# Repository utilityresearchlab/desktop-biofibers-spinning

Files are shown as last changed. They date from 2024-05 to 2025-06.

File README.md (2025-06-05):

# Desktop Biofibers Spinning Machine v1.0.1

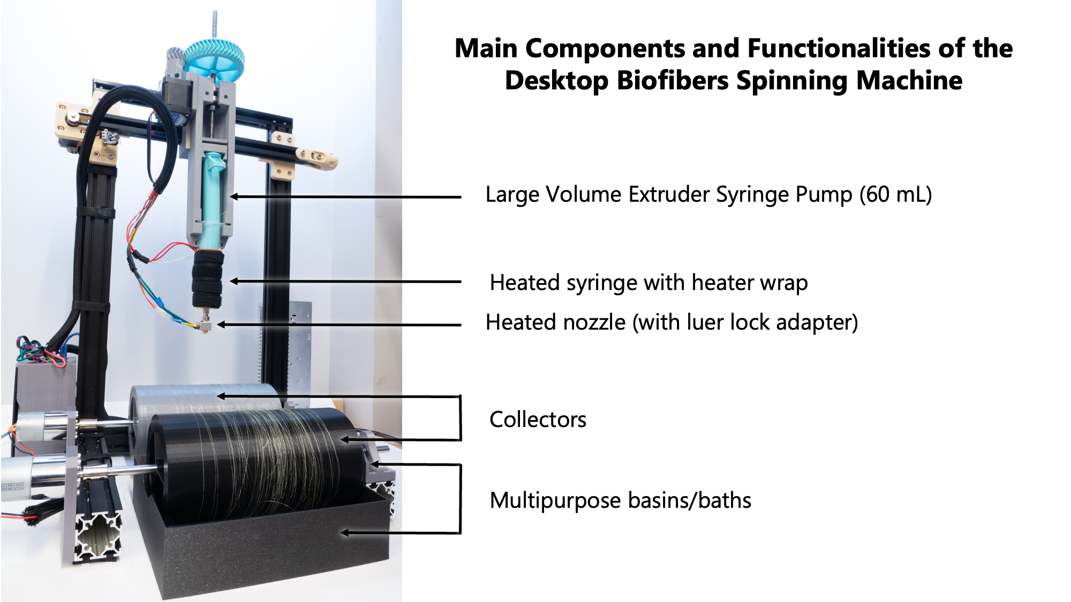
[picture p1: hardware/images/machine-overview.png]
Machine Overview


The Desktop Biofibers Spinning Machine is an open-source, modular machine for producing textile fibers from sustainable bio-based liquid solutions. It enables prototyping new types of sustainable fibers and exploring the design of sustainable smart textiles.

It supports spinning fibers from bio-based solutions, including ones that require heat during the spinning process. 

This repository contains all the design-related details and files to build the machine.

## High-level Specifications
- ~$600 for a machine (and even less if you reuse an old 3D printer like an Ender 3v2!)
- Heated Syringe Wrap
- 60 mL Syringe Volume (using the Open-Source Large Volume Extruder)
- Supports Luer Lock Nozzles/Tips
- Supports Heated Nozzle using a Luer Lock-to-M6 3D printer nozzle adapter
- Modular collector assemblies for applying different coatings to fibers

## Building a Biofibers Machine
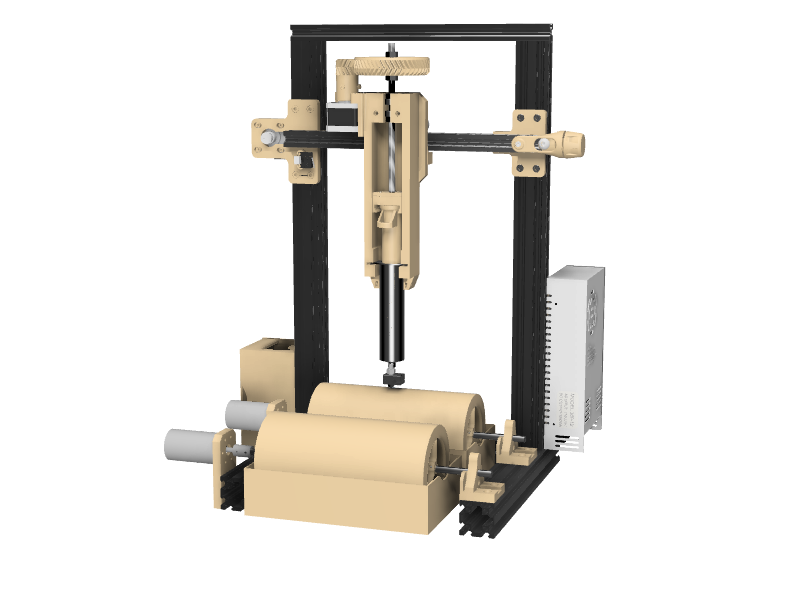
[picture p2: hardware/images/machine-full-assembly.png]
Machine Diagram with Printed Parts in Tan


- [Bill of Materials](https://docs.google.com/spreadsheets/d/1E_2IHzlC_cG40hGRjpHroCwSM1nkIKEBkRHdSb38-pU/edit#gid=0)
- Download the repository
- 3D Print the parts as listed in the BoM. Unless otherwise noted in the BoM Description/Notes, all 3D printed parts should be printed using PLA, 20% infill, 0.2 mm Layer height. The default "quality" setting in Prusa Slicer for the MK3S+/mini+ should be sufficient. The printed parts are shown in the color tan in the diagram above.

- Download the [CAD Assembly for Fusion 360](https://drive.google.com/drive/folders/1Qh19Er5d5Sq22oTk4Mabvu63gKj0vlPQ?usp=sharing) for assembly guidance and connect with us on Discord (see info below)
- Follow the [Electronics Wiring Diagram](https://github.com/utilityresearchlab/desktop-biofibers-spinning/blob/main/hardware/electronics-assembly/biofibers-electronics-wiring-diagram-v1.0.1.jpg) alongside the
  [RAMPS 1.4 Pin Out Schematic](https://github.com/utilityresearchlab/desktop-biofibers-spinning/blob/main/hardware/electronics-assembly/RAMPS%201.4/RAMPS1.4-PinOut-Schematic.png).

Electronics Wiring Diagram for the Biofibers Machine

- Follow our [work-in-progress assembly guide](https://docs.google.com/document/d/1JrAbMuTHmfADzdMDxia9Z5dNtl7umH7gnYQXavgpXdA/edit?tab=t.0#heading=h.pwn6s3sev8zz) for more instructions. 

## Using the Machine
We first recommend reviewing our [research paper](https://utilityresearchlab.org/assets/research/desktop-biofibers-spinning/chi24-desktop-biofibers-spinning.pdf) for more details on the fiber spinning process before using the machine.

To control the machine, we highly suggest using our open-source tool for MacOS and Windows available on our [Biofibers Machine Control repository](https://github.com/utilityresearchlab/biofibers-machine-control/). It streamlines setting up the machine as well as performing pull downs and the spinning procedure. You can do all of this without writing any g-code commands!

Screenshot 2025-05-24 at 10 03 42 PM

Alternatively, you may use any 3D printer host controller software like [Repetier Host](https://www.repetier.com/download-software/) to communicate with the machine. In your host controller software, set the baud rate to `250000`, and connect as you would a typical 3D printer. You can then use g-code commands to set the temperature of the syringe heater and nozzle, as well as set the collector speed/direction. More details are in the paper linked above.
   
## Join Our Discord for Assembly Help and Collaborations
We're eager to help and collaborate 😃! If you would like to work with us on the machine, build one yourself, or explore bio-based material solutions for fiber spinning, join our Discord: [https://discord.gg/vDmk3t2FMX](https://discord.gg/vDmk3t2FMX). For all other inquires, please reach out to 
 reach out to [Dr. Michael Rivera](https://mikeriv.com) and the [Utility Research Lab](https://utilityresearchlab.org).
 
## Planned Updates
- Movable Z-Axis
- ~Software Tool for Machine Control (for now a 3D printer host controller works to send G-code commands)~
- Custom Collector Shapes
- Assembly guides - [WIP Guide Here](https://docs.google.com/document/d/1JrAbMuTHmfADzdMDxia9Z5dNtl7umH7gnYQXavgpXdA/edit?tab=t.0#heading=h.pwn6s3sev8zz)

## Machine Design Change Log
- v1.0.1:
    - 2025-05-24:
      - Release Machine Control Desktop Application for MacOS and Windows    
    - 2024-11-30:
        - Added Electronics Wiring Diagram
    - 2024-11-07: 
        - Added new collector spindle v2.0.0 design with a key shaft lock
        - Added new LVE Small Gear v2 design
- v1.0.0: Initial design

## Paper Reference 
```
Eldy S. Lazaro Vasquez, Mirela Alistar, Laura Devendorf, and Michael L. Rivera. 2024. Desktop Biofibers Spinning: An Open-Source Machine for Exploring Biobased Fibers and Their Application Towards Sustainable Smart Textile Design. In Proceedings of the CHI Conference on Human Factors in Computing Systems (CHI '24). Association for Computing Machinery, New York, NY, USA, Article 856, 1–18. https://doi.org/10.1145/3613904.3642387
```

## Acknowledgements
This work is partially supported by the National Science Foundation under [Grant #241361](https://www.nsf.gov/awardsearch/showAward?AWD_ID=2413631&HistoricalAwards=false), [Grant #1943109](https://www.nsf.gov/awardsearch/showAward?AWD_ID=1943109&HistoricalAwards=false), and under Grant #2127309 to the
Computing Research Association for the CIFellows 2021 Project.
We are grateful to Simon Kammler, Daniel Wolters, Maximilian
Mohr, Stefan Peterek, Dr. Kazim Acatay, and research assistants at
the Institut für Textiltechnik (ITA) of RWTH Aachen University for
working with us as we explored fiber wet-spinning in their facilities. We are thankful to Philipp R. Stoessel for explaining his previous work with gelatin fibers wet spinning in very simple words which allowed us to replicate his spinning solution formulation. We would also like to acknowledge the support of Miles Henry Lewis who helped with designing and 3D printing the very first version of this machine.

### Open Source Projects
This machine leverages several open-source projects including the [RepRap RAMPS 1.4](https://reprap.org/wiki/RAMPS_1.4) under GPL v3 License, the [Marlin 2.1.1 firmware](https://marlinfw.org/) under GPL license, the [Large Volume Extruder](https://3d.nih.gov/entries/3DPX-008366) under CC-BY-SA 4.0, and the [Ender 3 V2 X axis belt tensioner replacement](https://www.printables.com/model/309148-ender-3-v2-x-axis-belt-tensioner-replacement) under CC-BY-NC-SA 4.0. The associated licenses can be found in the relevant folders of this repository.
##

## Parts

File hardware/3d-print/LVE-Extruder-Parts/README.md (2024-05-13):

# Original LVE Design is from https://3d.nih.gov/entries/3DPX-008366

# License: https://creativecommons.org/licenses/by-sa/4.0/

# Changes:
- Redesigned the Small gear (LVE_Small_Gear_v2.stl) to have a D-shaft and drop-in M3 nuts for a more secure fit.

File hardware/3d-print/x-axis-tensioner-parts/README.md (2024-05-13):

Original Design is "Ender 3 V2 X axis belt tensioner replacement" on Printables: 

- https://www.printables.com/model/309148-ender-3-v2-x-axis-belt-tensioner-replacement

- License: https://creativecommons.org/licenses/by-nc-sa/4.0/

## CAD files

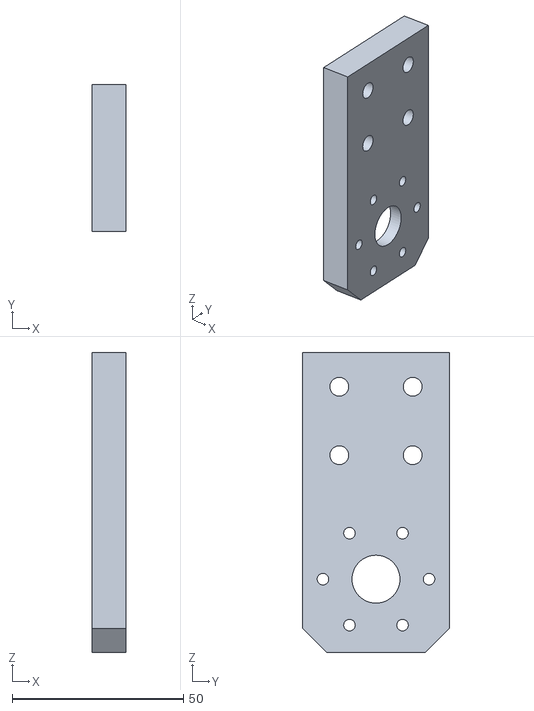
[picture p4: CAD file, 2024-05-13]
hardware/3d-print/collector-assembly/DC-Motor-Vertical Mount-10_RPM.stl
10.0 x 42.9 x 87.6

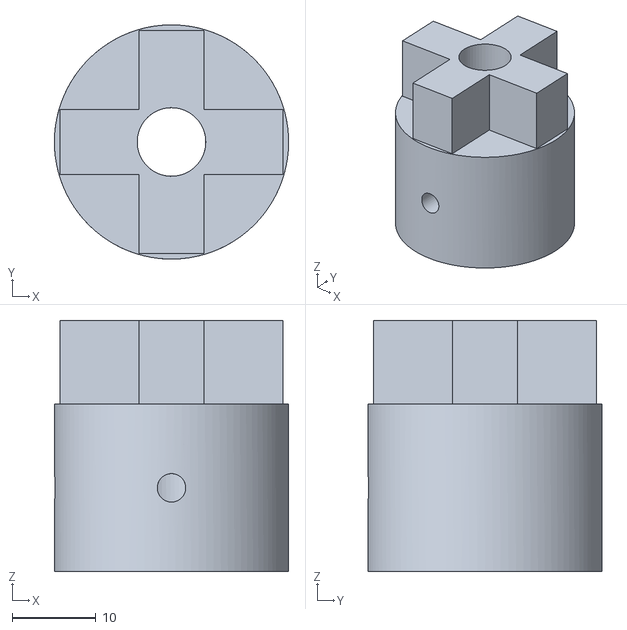
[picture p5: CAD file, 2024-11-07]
hardware/3d-print/collector-assembly/spindle-collector-v2.0.0/spindle-collector-_key-shaft-lock-v2.0.0.stl
28.0 x 28.0 x 30.0

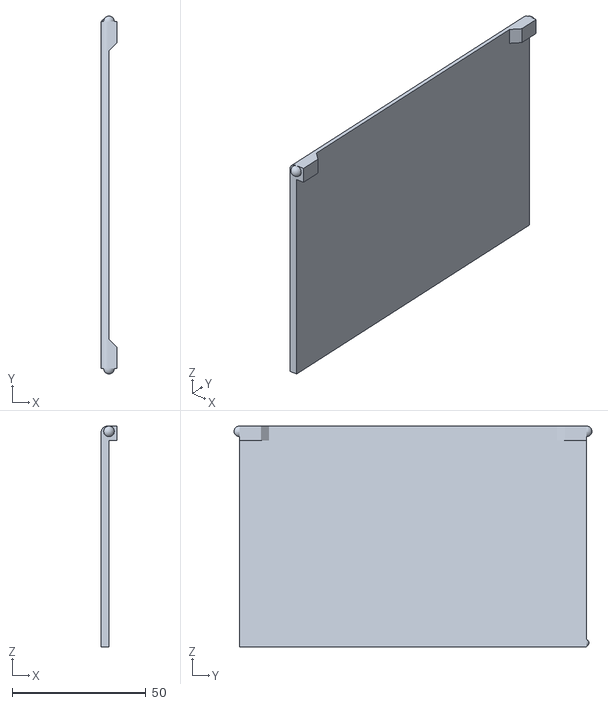
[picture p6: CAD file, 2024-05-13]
hardware/3d-print/electronics-enclosure/ramps-1.4-enclosure-door.stl
6.00 x 133.6 x 82.5

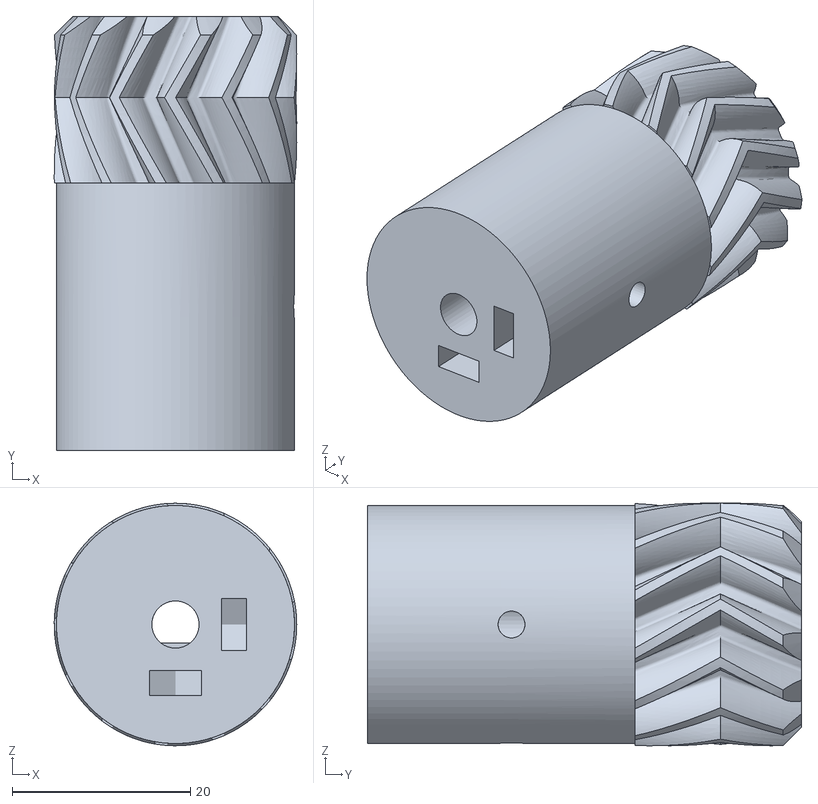
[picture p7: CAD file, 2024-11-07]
hardware/3d-print/LVE-Extruder-Parts/LVE_Small_Gear-v2.stl
27.2 x 48.7 x 27.2

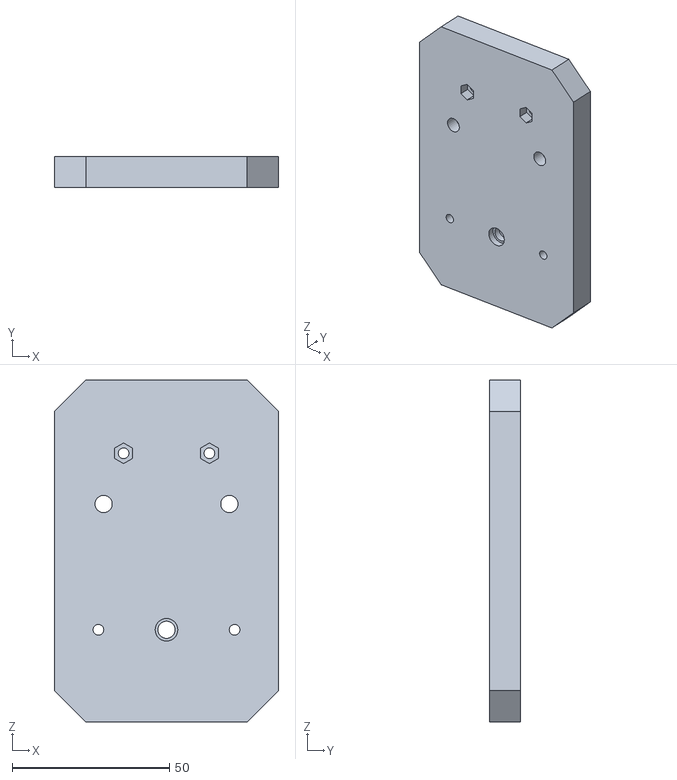
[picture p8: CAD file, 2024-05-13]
hardware/3d-print/x-axis-carriage/x-axis-carriage-syringe-adapter-v1.stl
71.3 x 10.0 x 108.8

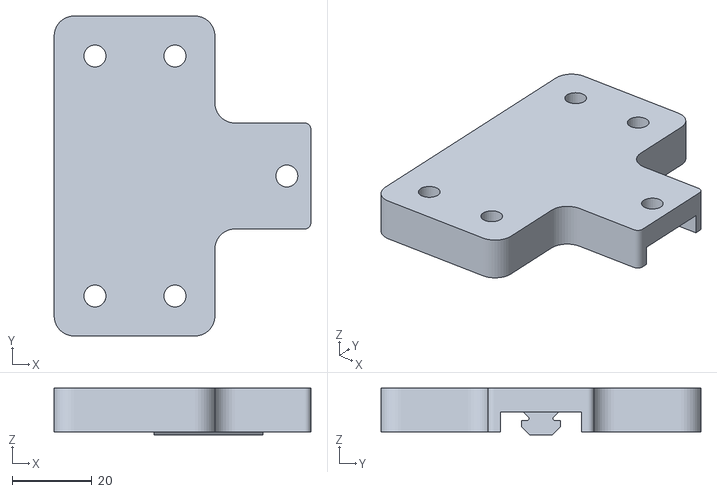
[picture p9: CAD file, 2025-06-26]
hardware/3d-print/x-axis-mount-right.stl
64.2 x 80.0 x 11.7

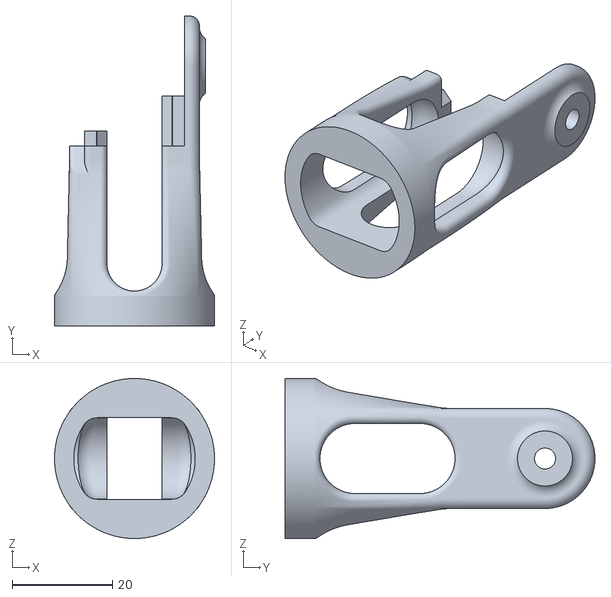
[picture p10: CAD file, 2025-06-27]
hardware/3d-print/x-axis-tensioner-parts/x-tensioner-body.stl
32.0 x 62.0 x 32.0

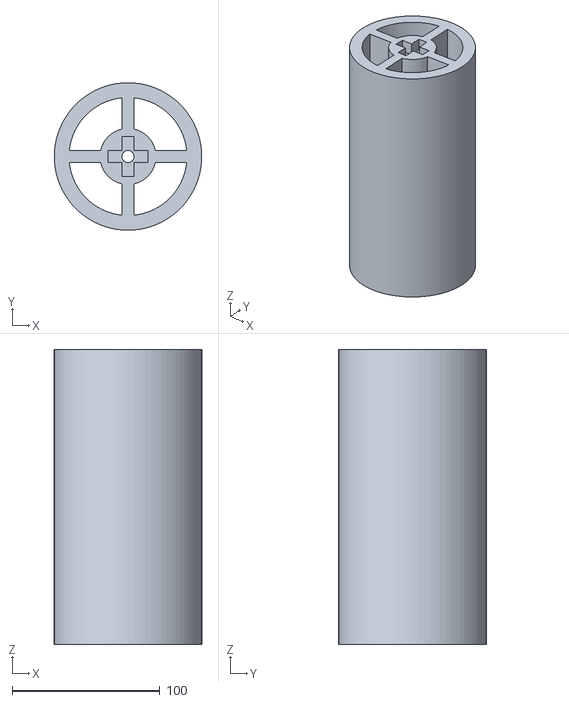
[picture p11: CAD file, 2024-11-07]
hardware/3d-print/collector-assembly/spindle-collector-v2.0.0/spindle-collector-keyed-body-v2.0.0.stl
100.0 x 100.0 x 200.0

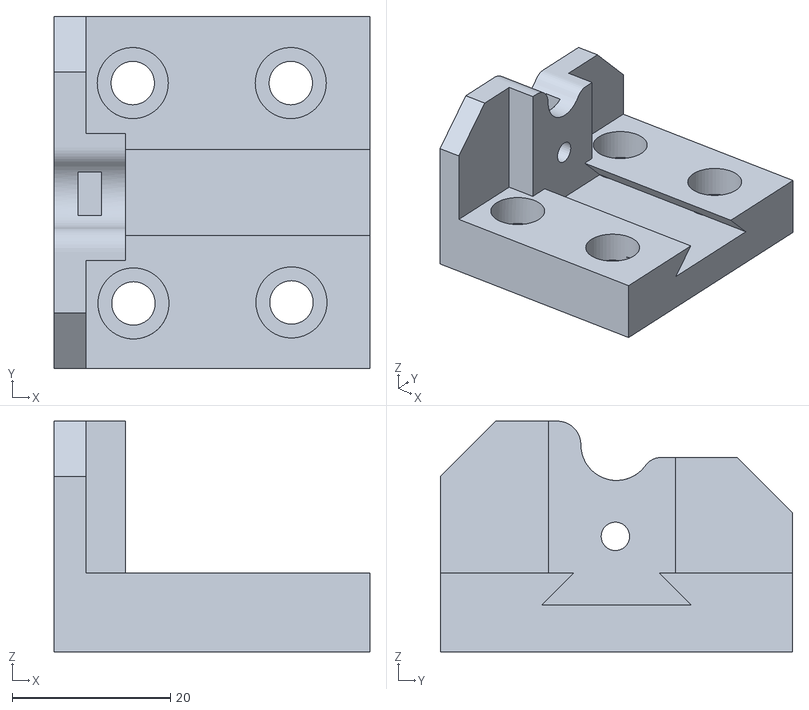
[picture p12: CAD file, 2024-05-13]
hardware/3d-print/collector-assembly/Spindle-idler-mount.stl
39.9 x 44.6 x 29.2

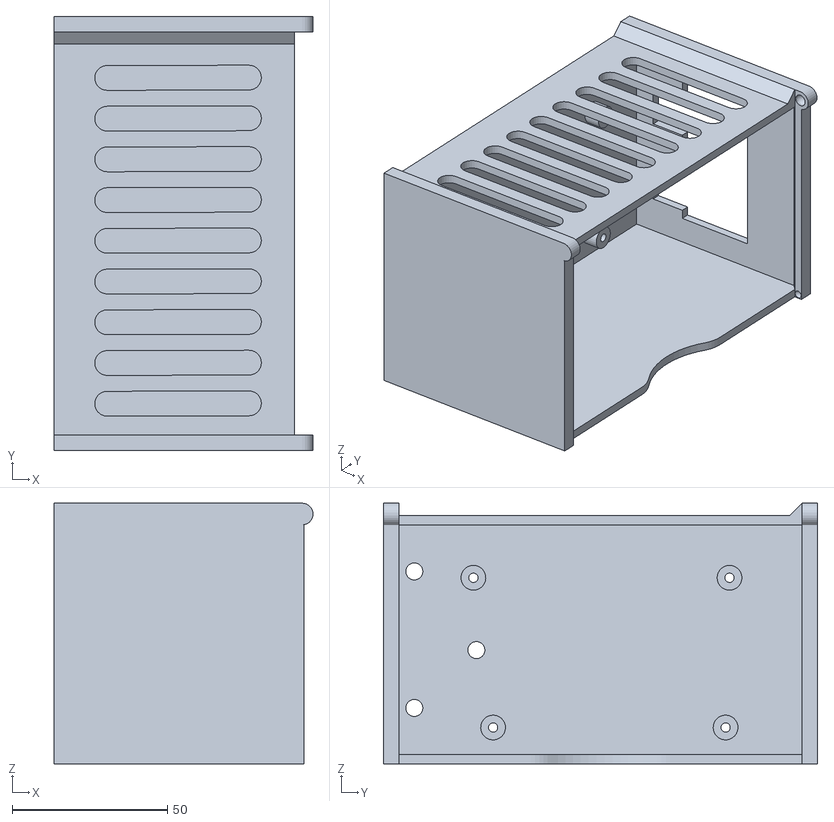
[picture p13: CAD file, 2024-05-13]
hardware/3d-print/electronics-enclosure/ramps-1.4-enclosure-body.stl
83.5 x 140.0 x 84.0

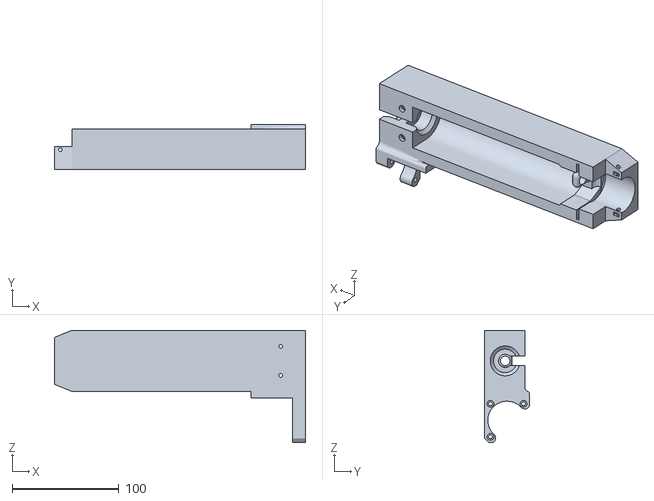
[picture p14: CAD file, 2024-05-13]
hardware/3d-print/LVE-Extruder-Parts/core.stl
235.6 x 42.1 x 105.6

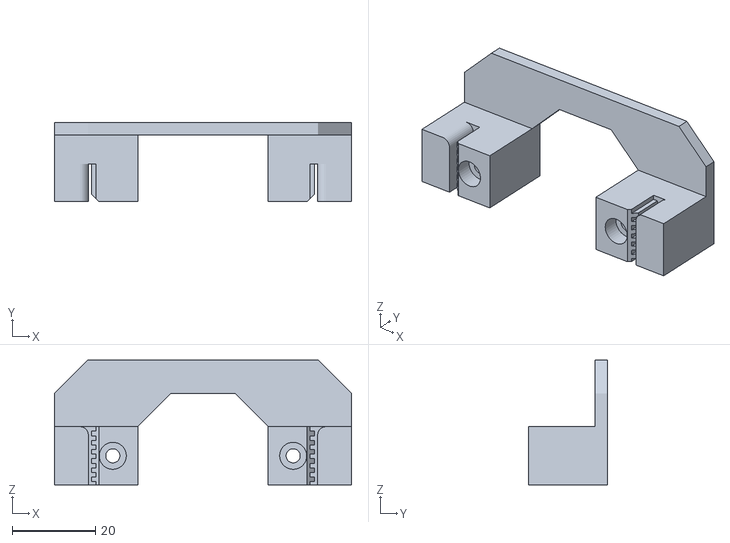
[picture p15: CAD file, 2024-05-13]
hardware/3d-print/x-axis-carriage/x-axis-carriage-belt-adapter-v1.stl
71.3 x 19.0 x 30.0

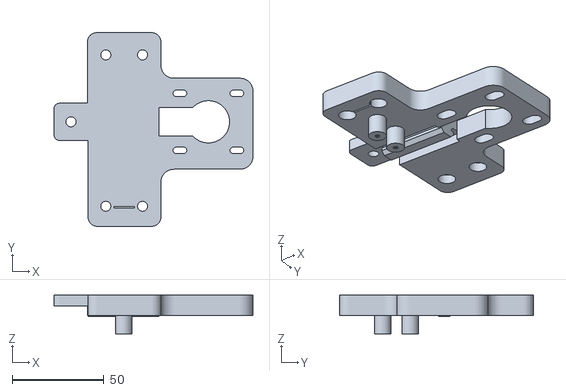
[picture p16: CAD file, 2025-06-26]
hardware/3d-print/x-axis-mount-left.stl
108.3 x 105.4 x 21.0

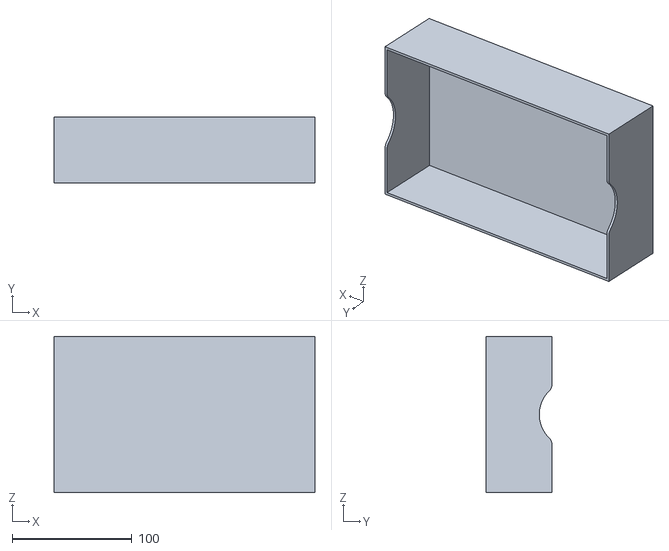
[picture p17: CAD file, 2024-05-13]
hardware/3d-print/collector-assembly/spindle-collector-tray.stl
218.0 x 55.0 x 130.6

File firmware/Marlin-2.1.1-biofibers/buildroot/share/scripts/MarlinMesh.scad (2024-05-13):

 /**************************************\
 *                                      *
 *   OpenSCAD Mesh Display              *
 *   by Thinkyhead - April 2017         *
 *                                      *
 *   Copy the grid output from Marlin,  *
 *   paste below as shown, and use      *
 *   OpenSCAD to see a visualization    *
 *   of your mesh.                      *
 *                                      *
 \**************************************/

$t = 0.15; // comment out during animation!
X = 0; Y = 1;
L = 0; R = 1; F = 2; B = 3;

//
// Sample Mesh - Replace with your own
//
measured_z = [
  [ -1.20, -1.13, -1.09, -1.03, -1.19 ],
  [ -1.16, -1.25, -1.27, -1.25, -1.08 ],
  [ -1.13, -1.26, -1.39, -1.31, -1.18 ],
  [ -1.09, -1.20, -1.26, -1.21, -1.18 ],
  [ -1.13, -0.99, -1.03, -1.06, -1.32 ]
];

//
// An offset to add to all points in the mesh
//
zadjust     = 0;

//
// Mesh characteristics
//
bed_size = [ 200, 200 ];

mesh_inset  = [ 10, 10, 10, 10 ]; // L, F, R, B

mesh_bounds = [
  [ mesh_inset[L], mesh_inset[F] ],
  [ bed_size[X] - mesh_inset[R], bed_size[Y] - mesh_inset[B] ]
];

mesh_size = mesh_bounds[1] - mesh_bounds[0];

                      // NOTE: Marlin meshes already subtract the probe offset
NAN         = 0;      // Z to use for un-measured points

//
// Geometry
//

max_z_scale   = 100;   // Scale at Time 0.5
min_z_scale   = 10;    // Scale at Time 0.0 and 1.0
thickness     = 0.5;   // thickness of the mesh triangles
tesselation   = 1;     // levels of tesselation from 0-2
alternation   = 2;     // direction change modulus (try it)

//
// Appearance
//

show_plane    = true;
show_labels   = true;
show_coords   = true;
arrow_length  = 5;

label_font_lg = "Arial";
label_font_sm = "Arial";
mesh_color    = [1,1,1,0.5];
plane_color   = [0.4,0.6,0.9,0.6];

//================================================ Derive useful values

big_z = max_2D(measured_z,0);
lil_z = min_2D(measured_z,0);

mean_value = (big_z + lil_z) / 2.0;

mesh_points_y = len(measured_z);
mesh_points_x = len(measured_z[0]);

xspace = mesh_size[X] / (mesh_points_x - 1);
yspace = mesh_size[Y] / (mesh_points_y - 1);

// At $t=0 and $t=1 scale will be 100%
z_scale_factor = min_z_scale + (($t > 0.5) ? 1.0 - $t : $t) * (max_z_scale - min_z_scale) * 2;

//
// Min and max recursive functions for 1D and 2D arrays
// Return the smallest or largest value in the array
//
function some_1D(b,i) = (i<len(b)-1) ? (b[i] && some_1D(b,i+1)) : b[i] != 0;
function some_2D(a,j) = (j<len(a)-1) ? some_2D(a,j+1) : some_1D(a[j], 0);
function min_1D(b,i) = (i<len(b)-1) ? min(b[i], min_1D(b,i+1)) : b[i];
function min_2D(a,j) = (j<len(a)-1) ? min_2D(a,j+1) : min_1D(a[j], 0);
function max_1D(b,i) = (i<len(b)-1) ? max(b[i], max_1D(b,i+1)) : b[i];
function max_2D(a,j) = (j<len(a)-1) ? max_2D(a,j+1) : max_1D(a[j], 0);

//
// Get the corner probe points of a grid square.
//
// Input  : x,y grid indexes
// Output : An array of the 4 corner points
//
function grid_square(x,y) = [
  [x * xspace, y * yspace, z_scale_factor * (measured_z[y][x] - mean_value)],
  [x * xspace, (y+1) * yspace, z_scale_factor * (measured_z[y+1][x] - mean_value)],
  [(x+1) * xspace, (y+1) * yspace, z_scale_factor * (measured_z[y+1][x+1] - mean_value)],
  [(x+1) * xspace, y * yspace, z_scale_factor * (measured_z[y][x+1] - mean_value)]
];

// The corner point of a grid square with Z centered on the mean
function pos(x,y,z) = [x * xspace, y * yspace, z_scale_factor * (z - mean_value)];

//
// Draw the point markers and labels
//
module point_markers(show_home=true) {
  // Mark the home position 0,0
  if (show_home)
    translate([1,1]) color([0,0,0,0.25])
      cylinder(r=1, h=z_scale_factor, center=true);

  for (x=[0:mesh_points_x-1], y=[0:mesh_points_y-1]) {
    z = measured_z[y][x] - zadjust;
    down = z < mean_value;
    xyz = pos(x, y, z);
    translate([ xyz[0], xyz[1] ]) {

      // Show the XY as well as the Z!
      if (show_coords) {
        color("black")
        translate([0,0,0.5]) {
          $fn=8;
          rotate([0,0]) {
            posx = floor(mesh_bounds[0][X] + x * xspace);
            posy = floor(mesh_bounds[0][Y] + y * yspace);
            text(str(posx, ",", posy), 2, label_font_sm, halign="center", valign="center");
          }
        }
      }

      translate([ 0, 0, xyz[2] ]) {
        // Label each point with the Z
        v = z - mean_value;
        if (show_labels) {

          color(abs(v) < 0.1 ? [0,0.5,0] : [0.25,0,0])
          translate([0,0,down?-10:10]) {

            $fn=8;
            rotate([90,0])
              text(str(z), 6, label_font_lg, halign="center", valign="center");

            if (v)
              translate([0,0,down?-6:6]) rotate([90,0])
                text(str(down || !v ? "" : "+", v), 3, label_font_sm, halign="center", valign="center");
          }
        }

        // Show an arrow pointing up or down
        if (v) {
          rotate([0, down ? 180 : 0]) translate([0,0,-1])
            cylinder(
              r1=0.5,
              r2=0.1,
              h=arrow_length, $fn=12, center=1
            );
        }
        else
          color([1,0,1,0.4]) sphere(r=1.0, $fn=20, center=1);
      }
    }
  }
}

//
// Split a square on the diagonal into
// two triangles and render them.
//
//     s : a square
//   alt : a flag to split on the other diagonal
//
module tesselated_square(s, alt=false) {
  add = [0,0,thickness];
  p1 = [
    s[0], s[1], s[2], s[3],
    s[0]+add, s[1]+add, s[2]+add, s[3]+add
  ];
  f1 = alt
      ? [ [0,1,3], [4,5,1,0], [4,7,5], [5,7,3,1], [7,4,0,3] ]
      : [ [0,1,2], [4,5,1,0], [4,6,5], [5,6,2,1], [6,4,0,2] ];
  f2 = alt
      ? [ [1,2,3], [5,6,2,1], [5,6,7], [6,7,3,2], [7,5,1,3] ]
      : [ [0,2,3], [4,6,2,0], [4,7,6], [6,7,3,2], [7,4,0,3] ];

  // Use the other diagonal
  polyhedron(points=p1, faces=f1);
  polyhedron(points=p1, faces=f2);
}

/**
 * The simplest mesh display
 */
module simple_mesh(show_plane=show_plane) {
  if (show_plane) color(plane_color) cube([mesh_size[X], mesh_size[Y], thickness]);
  color(mesh_color)
    for (x=[0:mesh_points_x-2], y=[0:mesh_points_y-2])
      tesselated_square(grid_square(x, y));
}

/**
 * Subdivide the mesh into smaller squares.
 */
module bilinear_mesh(show_plane=show_plane,tesselation=tesselation) {
  if (show_plane) color(plane_color) translate([-5,-5]) cube([mesh_size[X]+10, mesh_size[Y]+10, thickness]);

  if (some_2D(measured_z, 0)) {

    tesselation = tesselation % 4;
    color(mesh_color)
    for (x=[0:mesh_points_x-2], y=[0:mesh_points_y-2]) {
      square = grid_square(x, y);
      if (tesselation < 1) {
        tesselated_square(square,(x%alternation)-(y%alternation));
      }
      else {
        subdiv_4 = subdivided_square(square);
        if (tesselation < 2) {
          for (i=[0:3]) tesselated_square(subdiv_4[i],i%alternation);
        }
        else {
          for (i=[0:3]) {
            subdiv_16 = subdivided_square(subdiv_4[i]);
            if (tesselation < 3) {
              for (j=[0:3]) tesselated_square(subdiv_16[j],j%alternation);
            }
            else {
              for (j=[0:3]) {
                subdiv_64 = subdivided_square(subdiv_16[j]);
                if (tesselation < 4) {
                  for (k=[0:3]) tesselated_square(subdiv_64[k]);
                }
              }
            }
          }
        }
      }
    }

  }
}

//
// Subdivision helpers
//
function ctrz(a) = (a[0][2]+a[1][2]+a[3][2]+a[2][2])/4;
function avgx(a,i) = (a[i][0]+a[(i+1)%4][0])/2;
function avgy(a,i) = (a[i][1]+a[(i+1)%4][1])/2;
function avgz(a,i) = (a[i][2]+a[(i+1)%4][2])/2;

//
// Convert one square into 4, applying bilinear averaging
//
// Input  : 1 square (4 points)
// Output : An array of 4 squares
//
function subdivided_square(a) = [
  [ // SW square
    a[0],                          // SW
    [a[0][0],avgy(a,0),avgz(a,0)], // CW
    [avgx(a,1),avgy(a,0),ctrz(a)], // CC
    [avgx(a,1),a[0][1],avgz(a,3)]  // SC
  ],
  [ // NW square
    [a[0][0],avgy(a,0),avgz(a,0)], // CW
    a[1],                          // NW
    [avgx(a,1),a[1][1],avgz(a,1)], // NC
    [avgx(a,1),avgy(a,0),ctrz(a)]  // CC
  ],
  [ // NE square
    [avgx(a,1),avgy(a,0),ctrz(a)], // CC
    [avgx(a,1),a[1][1],avgz(a,1)], // NC
    a[2],                          // NE
    [a[2][0],avgy(a,0),avgz(a,2)]  // CE
  ],
  [ // SE square
    [avgx(a,1),a[0][1],avgz(a,3)], // SC
    [avgx(a,1),avgy(a,0),ctrz(a)], // CC
    [a[2][0],avgy(a,0),avgz(a,2)], // CE
    a[3]                           // SE
  ]
];


//================================================ Run the plan

translate([-mesh_size[X] / 2, -mesh_size[Y] / 2]) {
  $fn = 12;
  point_markers();
  bilinear_mesh();
}

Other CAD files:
hardware/3d-print/LVE-Extruder-Parts/syringe plunger.stl
hardware/3d-print/power-supply-bracket.stl
hardware/3d-print/collector-assembly/spindle-collector.stl
hardware/3d-print/collector-assembly/Spindle-idler-lock.stl
hardware/3d-print/LVE-Extruder-Parts/big gear.stl
hardware/3d-print/LVE-Extruder-Parts/nut shuttle plate.stl
hardware/3d-print/LVE-Extruder-Parts/nut shuttle.stl
hardware/3d-print/collector-assembly/archived/spindle-collector-v1.0.0/spindle-collector-v1.0.0.stl

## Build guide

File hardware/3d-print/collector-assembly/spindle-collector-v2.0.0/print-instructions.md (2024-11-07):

# Print Instructions
There are two parts to this spindle - the keyed body and the key-shaft-lock.

1. For the spindle body:
- Infill: 15%, gyroid
- Use support material

2. For the Key-Shaft Lock:
- Infill: 20%, gyroid
- Use support Material (though could be likely be printed without)

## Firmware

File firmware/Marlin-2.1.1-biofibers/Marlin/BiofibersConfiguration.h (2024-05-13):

#pragma once 

#define ENABLE_BF_SPINDLE true

// Comment to hide debugging info
//#define DEBUG_BF_SPINDLE

// Driver is a Adafruit TB6612 
#define BF_SPINDLE_DRIVER_STBY_PIN 42

#define BF_SPINDLE_DRIVER_PWM_A_PIN 44
#define BF_SPINDLE_DRIVER_AIN1_PIN  40
#define BF_SPINDLE_DRIVER_AIN2_PIN  63

#define BF_SPINDLE_DRIVER_PWM_B_PIN 6
#define BF_SPINDLE_DRIVER_BIN1_PIN 64
#define BF_SPINDLE_DRIVER_BIN2_PIN 59

// Configuration_adv settings 

#define BF_SPINDLE_ENABLE_ACTIVE_STATE HIGH

// comment out to remove PWM support 
#define BF_SPINDLE_USE_PWM 
#define BF_SPINDLE_DRIVER_CHANGE_DIR true
#define BF_SPINDLE_DRIVER_CHANGE_DIR_STOP true
#define BF_SPINDLE_DRIVER_INVERT_DIR false

#define BF_SPINDLE_DRIVER_POWERON_DELAY 5000 // ms
#define BF_SPINDLE_DRIVER_POWEROFF_DELAY 5000 // ms

#define BF_SPINDLE_FREQUENCY 500 // 2500 original
#define BF_SPINDLE_SPEED_RPM_MIN 0
#define BF_SPINDLE_SPEED_RPM_MAX 10
#define BF_SPINDLE_SPEED_RPM_START 1 // M3/M4 speed with no command


/**
 * Speed / Power can be set ('M3 S') and displayed in terms of:
 *  - PWM255  (S0 - S255)
 *  - PERCENT (S0 - S100)
 *  - RPM     (S0 - S50000)  Best for use with a spindle
 *  - SERVO   (S0 - S180)
 */

#define BF_SPINDLE_POWER_UNIT PWM255 

// The set up below is what is used in spindle_laser.cpp
#define SPINDLE_PWM_A_PIN         BF_SPINDLE_DRIVER_PWM_A_PIN  
#define SPINDLE_DIR_A1_PIN        BF_SPINDLE_DRIVER_AIN1_PIN
#define SPINDLE_DIR_A2_PIN        BF_SPINDLE_DRIVER_AIN2_PIN

#define SPINDLE_PWM_B_PIN         BF_SPINDLE_DRIVER_PWM_B_PIN  
#define SPINDLE_DIR_B1_PIN        BF_SPINDLE_DRIVER_BIN1_PIN
#define SPINDLE_DIR_B2_PIN        BF_SPINDLE_DRIVER_BIN2_PIN


// Note the pins in this file override defaults in pins_RAMPS.h)
// set default pins for marlin to behave and know we have a spindle 
// Specifically the pins: 
//  SPINDLE_LASER_ENA_PIN
//  SPINDLE_LASER_PWM_PIN   
//  SPINDLE_DIR_PIN      

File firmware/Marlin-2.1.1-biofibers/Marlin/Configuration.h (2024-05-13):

/**
 * Marlin 3D Printer Firmware
 * Copyright (c) 2020 MarlinFirmware [https://github.com/MarlinFirmware/Marlin]
 *
 * Based on Sprinter and grbl.
 * Copyright (c) 2011 Camiel Gubbels / Erik van der Zalm
 *
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
 */
#pragma once
/**
 * Configuration.h
 *
 * Basic settings such as:
 *
 * - Type of electronics
 * - Type of temperature sensor
 * - Printer geometry
 * - Endstop configuration
 * - LCD controller
 * - Extra features
 *
 * Advanced settings can be found in Configuration_adv.h
 */
#define CONFIGURATION_H_VERSION 02010100

//===========================================================================
//============================= Getting Started =============================
//===========================================================================

/**
 * Here are some useful links to help get your machine configured and calibrated:
 *
 * Example Configs:     https://github.com/MarlinFirmware/Configurations/branches/all
 *
 * Průša Calculator:    https://blog.prusaprinters.org/calculator_3416/
 *
 * Calibration Guides:  https://reprap.org/wiki/Calibration
 *                      https://reprap.org/wiki/Triffid_Hunter%27s_Calibration_Guide
 *                      https://sites.google.com/site/repraplogphase/calibration-of-your-reprap
 *                      https://youtu.be/wAL9d7FgInk
 *
 * Calibration Objects: https://www.thingiverse.com/thing:5573
 *                      https://www.thingiverse.com/thing:1278865
 */

// @section info

// Author info of this build printed to the host during boot and M115
#define STRING_CONFIG_H_AUTHOR "(none, default config)" // Who made the changes.
//#define CUSTOM_VERSION_FILE Version.h // Path from the root directory (no quotes)

/**
 * *** VENDORS PLEASE READ ***
 *
 * Marlin allows you to add a custom boot image for Graphical LCDs.
 * With this option Marlin will first show your custom screen followed
 * by the standard Marlin logo with version number and web URL.
 *
 * We encourage you to take advantage of this new feature and we also
 * respectfully request that you retain the unmodified Marlin boot screen.
 */

// Show the Marlin bootscreen on startup. ** ENABLE FOR PRODUCTION **
#define SHOW_BOOTSCREEN

// Show the bitmap in Marlin/_Bootscreen.h on startup.
//#define SHOW_CUSTOM_BOOTSCREEN

// Show the bitmap in Marlin/_Statusscreen.h on the status screen.
//#define CUSTOM_STATUS_SCREEN_IMAGE

// @section machine

// Choose the name from boards.h that matches your setup
#ifndef MOTHERBOARD
  #define MOTHERBOARD BOARD_RAMPS_14_EEB
#endif

/**
 * Select the serial port on the board to use for communication with the host.
 * This allows the connection of wireless adapters (for instance) to non-default port pins.
 * Serial port -1 is the USB emulated serial port, if available.
 * Note: The first serial port (-1 or 0) will always be used by the Arduino bootloader.
 *
 * :[-1, 0, 1, 2, 3, 4, 5, 6, 7]
 */
#define SERIAL_PORT 0

/**
 * Serial Port Baud Rate
 * This is the default communication speed for all serial ports.
 * Set the baud rate defaults for additional serial ports below.
 *
 * 250000 works in most cases, but you might try a lower speed if
 * you commonly experience drop-outs during host printing.
 * You may try up to 1000000 to speed up SD file transfer.
 *
 * :[2400, 9600, 19200, 38400, 57600, 115200, 250000, 500000, 1000000]
 */
#define BAUDRATE 250000

//#define BAUD_RATE_GCODE     // Enable G-code M575 to set the baud rate

/**
 * Select a secondary serial port on the board to use for communication with the host.
 * Currently Ethernet (-2) is only supported on Teensy 4.1 boards.
 * :[-2, -1, 0, 1, 2, 3, 4, 5, 6, 7]
 */
//#define SERIAL_PORT_2 -1
//#define BAUDRATE_2 250000   // :[2400, 9600, 19200, 38400, 57600, 115200, 250000, 500000, 1000000] Enable to override BAUDRATE

/**
 * Select a third serial port on the board to use for communication with the host.
 * Currently only supported for AVR, DUE, LPC1768/9 and STM32/STM32F1
 * :[-1, 0, 1, 2, 3, 4, 5, 6, 7]
 */
//#define SERIAL_PORT_3 1
//#define BAUDRATE_3 250000   // :[2400, 9600, 19200, 38400, 57600, 115200, 250000, 500000, 1000000] Enable to override BAUDRATE

// Enable the Bluetooth serial interface on AT90USB devices
//#define BLUETOOTH

// Name displayed in the LCD "Ready" message and Info menu
//#define CUSTOM_MACHINE_NAME "3D Printer"

// Printer's unique ID, used by some programs to differentiate between machines.
// Choose your own or use a service like https://www.uuidgenerator.net/version4
//#define MACHINE_UUID "00000000-0000-0000-0000-000000000000"

/**
 * Stepper Drivers
 *
 * These settings allow Marlin to tune stepper driver timing and enable advanced options for
 * stepper drivers that support them. You may also override timing options in Configuration_adv.h.
 *
 * Use TMC2208/TMC2208_STANDALONE for TMC2225 drivers and TMC2209/TMC2209_STANDALONE for TMC2226 drivers.
 *
 * Options: A4988, A5984, DRV8825, LV8729, TB6560, TB6600, TMC2100,
 *          TMC2130, TMC2130_STANDALONE, TMC2160, TMC2160_STANDALONE,
 *          TMC2208, TMC2208_STANDALONE, TMC2209, TMC2209_STANDALONE,
 *          TMC26X,  TMC26X_STANDALONE,  TMC2660, TMC2660_STANDALONE,
 *          TMC5130, TMC5130_STANDALONE, TMC5160, TMC5160_STANDALONE
 * :['A4988', 'A5984', 'DRV8825', 'LV8729', 'TB6560', 'TB6600', 'TMC2100', 'TMC2130', 'TMC2130_STANDALONE', 'TMC2160', 'TMC2160_STANDALONE', 'TMC2208', 'TMC2208_STANDALONE', 'TMC2209', 'TMC2209_STANDALONE', 'TMC26X', 'TMC26X_STANDALONE', 'TMC2660', 'TMC2660_STANDALONE', 'TMC5130', 'TMC5130_STANDALONE', 'TMC5160', 'TMC5160_STANDALONE']
 */
#define X_DRIVER_TYPE  A4988
#define Y_DRIVER_TYPE  A4988
#define Z_DRIVER_TYPE  A4988
//#define X2_DRIVER_TYPE A4988
//#define Y2_DRIVER_TYPE A4988
//#define Z2_DRIVER_TYPE A4988
//#define Z3_DRIVER_TYPE A4988
//#define Z4_DRIVER_TYPE A4988
//#define I_DRIVER_TYPE  A4988
//#define J_DRIVER_TYPE  A4988
//#define K_DRIVER_TYPE  A4988
//#define U_DRIVER_TYPE  A4988
//#define V_DRIVER_TYPE  A4988
//#define W_DRIVER_TYPE  A4988
#define E0_DRIVER_TYPE A4988
//#define E1_DRIVER_TYPE A4988
//#define E2_DRIVER_TYPE A4988
//#define E3_DRIVER_TYPE A4988
//#define E4_DRIVER_TYPE A4988
//#define E5_DRIVER_TYPE A4988
//#define E6_DRIVER_TYPE A4988
//#define E7_DRIVER_TYPE A4988

/**
 * Additional Axis Settings
 *
 * Define AXISn_ROTATES for all axes that rotate or pivot.
 * Rotational axis coordinates are expressed in degrees.
 *
 * AXISn_NAME defines the letter used to refer to the axis in (most) G-code commands.
 * By convention the names and roles are typically:
 *   'A' : Rotational axis parallel to X
 *   'B' : Rotational axis parallel to Y
 *   'C' : Rotational axis parallel to Z
 *   'U' : Secondary linear axis parallel to X
 *   'V' : Secondary linear axis parallel to Y
 *   'W' : Secondary linear axis parallel to Z
 *
 * Regardless of these settings the axes are internally named I, J, K, U, V, W.
 */
#ifdef I_DRIVER_TYPE
  #define AXIS4_NAME 'A' // :['A', 'B', 'C', 'U', 'V', 'W']
  #define AXIS4_ROTATES
#endif
#ifdef J_DRIVER_TYPE
  #define AXIS5_NAME 'B' // :['B', 'C', 'U', 'V', 'W']
  #define AXIS5_ROTATES
#endif
#ifdef K_DRIVER_TYPE
  #define AXIS6_NAME 'C' // :['C', 'U', 'V', 'W']
  #define AXIS6_ROTATES
#endif
#ifdef U_DRIVER_TYPE
  #define AXIS7_NAME 'U' // :['U', 'V', 'W']
  //#define AXIS7_ROTATES
#endif
#ifdef V_DRIVER_TYPE
  #define AXIS8_NAME 'V' // :['V', 'W']
  //#define AXIS8_ROTATES
#endif
#ifdef W_DRIVER_TYPE
  #define AXIS9_NAME 'W' // :['W']
  //#define AXIS9_ROTATES
#endif

// @section extruder

// This defines the number of extruders
// :[0, 1, 2, 3, 4, 5, 6, 7, 8]
#define EXTRUDERS 2

// Generally expected filament diameter (1.75, 2.85, 3.0, ...). Used for Volumetric, Filament Width Sensor, etc.
#define DEFAULT_NOMINAL_FILAMENT_DIA 1.75

// For Cyclops or any "multi-extruder" that shares a single nozzle.
//#define SINGLENOZZLE

// Save and restore temperature and fan speed on tool-change.
// Set standby for the unselected tool with M104/106/109 T...
#if ENABLED(SINGLENOZZLE)
  //#define SINGLENOZZLE_STANDBY_TEMP
  //#define SINGLENOZZLE_STANDBY_FAN
#endif

/**
 * Multi-Material Unit
 * Set to one of these predefined models:
 *
 *   PRUSA_MMU1           : Průša MMU1 (The "multiplexer" version)
 *   PRUSA_MMU2           : Průša MMU2
 *   PRUSA_MMU2S          : Průša MMU2S (Requires MK3S extruder with motion sensor, EXTRUDERS = 5)
 *   EXTENDABLE_EMU_MMU2  : MMU with configurable number of filaments (ERCF, SMuFF or similar with Průša MMU2 compatible firmware)
 *   EXTENDABLE_EMU_MMU2S : MMUS with configurable number of filaments (ERCF, SMuFF or similar with Průša MMU2 compatible firmware)
 *
 * Requires NOZZLE_PARK_FEATURE to park print head in case MMU unit fails.
 * See additional options in Configuration_adv.h.
 */
//#define MMU_MODEL PRUSA_MMU2

// A dual extruder that uses a single stepper motor
//#define SWITCHING_EXTRUDER
#if ENABLED(SWITCHING_EXTRUDER)
  #define SWITCHING_EXTRUDER_SERVO_NR 0
  #define SWITCHING_EXTRUDER_SERVO_ANGLES { 0, 90 } // Angles for E0, E1[, E2, E3]
  #if EXTRUDERS > 3
    #define SWITCHING_EXTRUDER_E23_SERVO_NR 1
  #endif
#endif

// A dual-nozzle that uses a servomotor to raise/lower one (or both) of the nozzles
//#define SWITCHING_NOZZLE
#if ENABLED(SWITCHING_NOZZLE)
  #define SWITCHING_NOZZLE_SERVO_NR 0
  //#define SWITCHING_NOZZLE_E1_SERVO_NR 1          // If two servos are used, the index of the second
  #define SWITCHING_NOZZLE_SERVO_ANGLES { 0, 90 }   // Angles for E0, E1 (single servo) or lowered/raised (dual servo)
  #define SWITCHING_NOZZLE_SERVO_DWELL 2500         // Dwell time to wait for servo to make physical move
#endif

/**
 * Two separate X-carriages with extruders that connect to a moving part
 * via a solenoid docking mechanism. Requires SOL1_PIN and SOL2_PIN.
 */
//#define PARKING_EXTRUDER

/**
 * Two separate X-carriages with extruders that connect to a moving part
 * via a magnetic docking mechanism using movements and no solenoid
 *
 * project   : https://www.thingiverse.com/thing:3080893
 * movements : https://youtu.be/0xCEiG9VS3k
 *             https://youtu.be/Bqbcs0CU2FE
 */
//#define MAGNETIC_PARKING_EXTRUDER

#if EITHER(PARKING_EXTRUDER, MAGNETIC_PARKING_EXTRUDER)

  #define PARKING_EXTRUDER_PARKING_X { -78, 184 }     // X positions for parking the extruders
  #define PARKING_EXTRUDER_GRAB_DISTANCE 1            // (mm) Distance to move beyond the parking point to grab the extruder

  #if ENABLED(PARKING_EXTRUDER)

    #define PARKING_EXTRUDER_SOLENOIDS_INVERT           // If enabled, the solenoid is NOT magnetized with applied voltage
    #define PARKING_EXTRUDER_SOLENOIDS_PINS_ACTIVE LOW  // LOW or HIGH pin signal energizes the coil
    #define PARKING_EXTRUDER_SOLENOIDS_DELAY 250        // (ms) Delay for magnetic field. No delay if 0 or not defined.
    //#define MANUAL_SOLENOID_CONTROL                   // Manual control of docking solenoids with M380 S / M381

  #elif ENABLED(MAGNETIC_PARKING_EXTRUDER)

    #define MPE_FAST_SPEED      9000      // (mm/min) Speed for travel before last distance point
    #define MPE_SLOW_SPEED      4500      // (mm/min) Speed for last distance travel to park and couple
    #define MPE_TRAVEL_DISTANCE   10      // (mm) Last distance point
    #define MPE_COMPENSATION       0      // Offset Compensation -1 , 0 , 1 (multiplier) only for coupling

  #endif

#endif

/**
 * Switching Toolhead
 *
 * Support for swappable and dockable toolheads, such as
 * the E3D Tool Changer. Toolheads are locked with a servo.
 */
//#define SWITCHING_TOOLHEAD

/**
 * Magnetic Switching Toolhead
 *
 * Support swappable and dockable toolheads with a magnetic
 * docking mechanism using movement and no servo.
 */
//#define MAGNETIC_SWITCHING_TOOLHEAD
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

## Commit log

2024-05-13 Initial commit for Biofibers Machine V1
    [DC-Motor-Vertical Mount-10_RPM.stl, LVE_Small_Gear-v2.stl, MarlinMesh.scad, Spindle-idler-lock.stl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]
2024-11-07 Add collector-spindle v2.0.0 with key shaft lock design; and archive v1.0.0
    [spindle-collector-_key-shaft-lock-v2.0.0.stl, spindle-collector-keyed-body-v2.0.0.stl, spindle-collector-v1.0.0.stl]
2024-11-07 Add LVE_Small_Gear-v2 design
    [LVE_Small_Gear-v2.stl]
2024-12-01 Add electronics wiring diagram from v1.0.1
2024-12-01 Update README.md with Wiring Diagram
2024-12-01 Rearrange Wiring Diagram Labels
2024-12-03 Add note about stepper wiring to electronics diagram
2025-06-26 Fix units to be millimeters on x-axis-mount-left and -right stl files.
    [x-axis-mount-left.stl, x-axis-mount-right.stl]
2025-06-27 Fix x-tensioner units to be mm instead of inches
    [x-tensioner-body.stl]
2025-10-01 fix x-tensioner screw insert model to be M5 size instead of M4

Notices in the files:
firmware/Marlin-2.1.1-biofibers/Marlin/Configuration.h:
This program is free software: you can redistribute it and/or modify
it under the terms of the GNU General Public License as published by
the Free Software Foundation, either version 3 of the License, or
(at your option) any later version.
